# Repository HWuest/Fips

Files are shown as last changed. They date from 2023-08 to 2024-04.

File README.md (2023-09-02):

# Fips
Fips, mobile communication device for deafblind people

Offen

## Motivation
The biggest problem for deafblind people is social isolation.
Ofcourse they can read books printed in Braille or write a letter using a Braille keyboard, but this is not the same as talking with somebody.
## The aim of the project
is to provide a technical solution which allows deafblind people to talk with somebody as similar to a normal talk as possible. 
## System architecture - Top Level
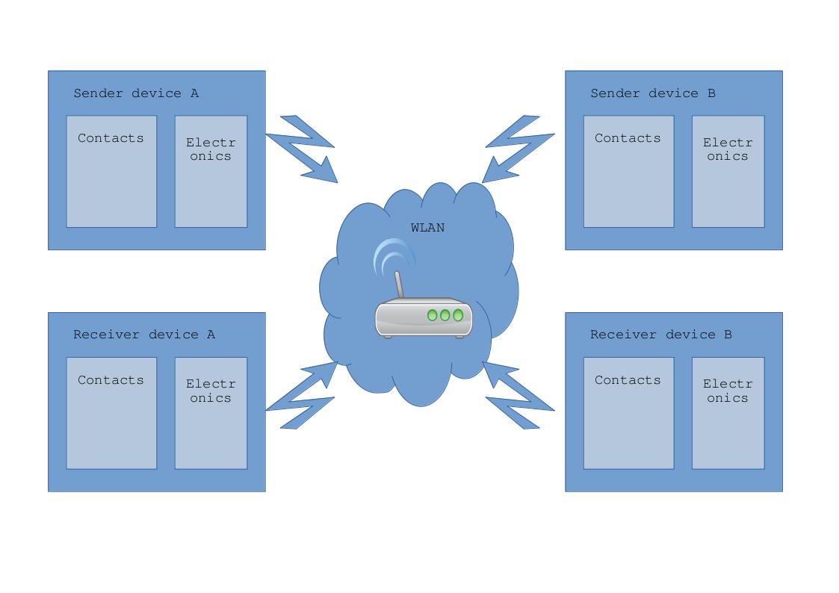
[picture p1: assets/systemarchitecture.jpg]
JPG image


## How to build

1. Get all hardware components from the partlist (see hardware folder)
2. Generate the 3D printing files for an available 3D printer from the .stl files in the 3D folder
3. Print the components (3 parts of the aktuators are needed 5 times)
4. Clue the magnets on the magnet holder and place them in the coil holder so that the magnet holder can move freely up and down in the coil holder
5. Clip the bootom of the coil holder on to the coil holder
6. Wind 500 windings of the cooper wire on each coil holder leaving two 5cm long wires outside for electrically connection
7. Remove the isolation half a centimeter from the ends of the wires (with sandpaper)
8. Test the functionality of the actuator with the battery and mark the polarity where the magnet moves upwards
9. Mount the charging electronics, the battery, the actuators, the switches and the microcontroller in the housing
10. Connect the electronic components and the driver IC acording to the schematic (see hardware folder)
11. Download the SW on the microcontroller -> [Link to description](bin/Readme.md)
12. Test the functionality: inputs done with the switches on the input side should imediatly be mirrored on the actuators on the output side
13. Fix all parts with screws and put the housing together, finaly fix it with screws

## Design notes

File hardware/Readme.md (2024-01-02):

## Hardware
We have a sender and a receiver device.

The schematics are fips-sender.pdf and fips-receiver.pdf.

The sender device has a printed circuit board for easier connection of parts.

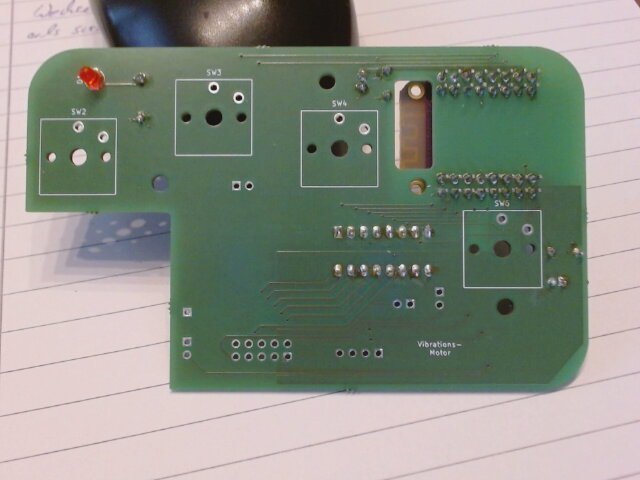
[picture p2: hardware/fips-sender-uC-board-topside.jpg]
top side
The top side of the board holds the keys and a LED (keys not shown in the picture 

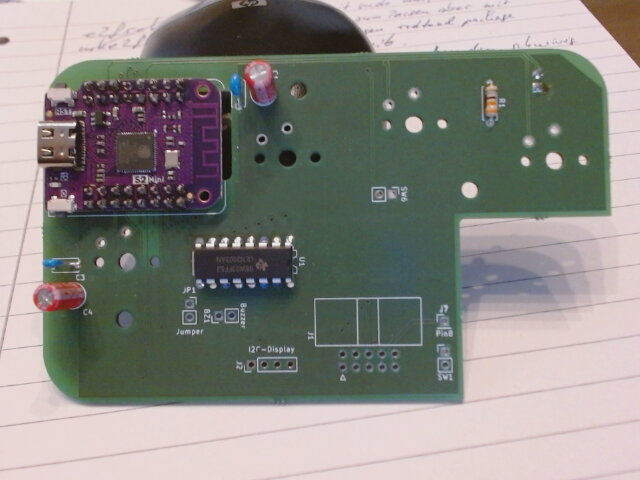
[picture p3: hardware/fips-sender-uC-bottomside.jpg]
top side
The bottom side holds the ESP32 microcontroller board and some other components.

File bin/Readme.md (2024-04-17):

## Latest ready to use binaries to flash on a ESP32S2 mini microcontroller board
- DeafBlind.bin
- bootloader.bin
- partition-table.bin
- (optional) ota_data_initial.bin 

## Beschreibung für das Flashen der Software (Programmierung des Mikrocontrollers)
Das Flashen der Software besteht aus mehreren Schritten.
- Das Flashen des Fips Programms für den ESP32, DeafBlind.bin
- Das Flashen des bootloaders, bootloader.bin
- Das Flashen der partition table, partition-table.bin
- (optional) Das Flashen von ota_data_inbitial.bin 
- Das Flashen der Dateien für die Webseiten auf dem ESP32
 
Zuerst müssen aber die Dateien vom github Server auf den lokalen Computer kopiert werden.
Dazu erst einen Ordner auf dem lokalen Computer anlegen, in dem alle notwendigen Dateien abgelegt werden sollen. 
Dann auf dieser Seite die Datei DeafBlind.bin anklicken. Dann oben rechts auf Download klicken und den Ordner auf dem lokalen Computer auswählen.
Wenn die Datei in den Download Ordner gespeichert wurde, die Datei von hier in den gewünschten Ordner ziehen.
Als zweites und drittes mit den Dateien bootloader.bin und partition-table.bin genauso verfahren. 

Zum Flashen des Fips Programms braucht man ein spezielles Flash Tool der Fa. Espressif. Es ist ein Python Programm und heisst esptool.py.
Die Installationsanweisung ist unter folgendem Link zu finden
`https://docs.espressif.com/projects/esptool/en/latest/esp32/installation.html#installation`

Bei Windows braucht man noch den Python Interpreter, damit sehen die Installationsschritte wie folgt aus.

1. Python installieren. Den Installer findet man unter `https://www.python.org/downloads/windows/`. Bei der Installation das Häkchen für die Anpassung der `PATH` Variablen setzen.
2. Das "esptool" installieren. Dazu mit `CMD` ein Terminal Fenster unter Windows aufmachen und folgenden Befehl eingeben: ```pip install esptool```.   

(Wir empfehlen, unser Script `fips-esptool` zu verwenden oder anzupassen, wenn die Dateien in anderen Ordnern liegen.)
```
python3 -m esptool --chip esp32s2 -b 460800 --before=default_reset --after=hard_reset write_flash --flash_mode dio --flash_freq 80m --flash_size 4MB 0x1000 bootloader.bin 0x10000 DeafBlind.bin 0x8000 partition-table.bin
```
oder optional mit ota - over the air - Programmierung: 

```
python3 -m esptool --chip esp32s2 -b 460800 --before=default_reset --after=hard_reset write_flash --flash_mode dio --flash_freq 80m --flash_size 4MB 0x1000 bootloader.bin 0x10000 DeafBlind.bin 0x8000 partition-table.bin 0xe000 ota_data_initial.bin
```

> Unter Linux ist Python standardmässig bereits installiert. Hier muss nur noch das esptool mit dem gleichen Kommando wie oben installiert werden. Eine > mögliche Fehlerquelle ist noch die installierte Python version, sie sollte grösser V3.7 sein. Die installierte Version erhält man mit dem Aufruf von `python --version` in der Kommandozeile. Wenn eine ältere Python Version installiert ist, kann man auf eine aktuelle Version upgraden, es sein denn.man braucht die ältere Version aus anderen Gründen. Ist das der Fall, gibt es kein Standard Vorgehen.  

Das Programm sucht automatisch nach dem richtigen USB Port. Wenn es den nicht findet und eine entsprechende Fehlermeldung ausgibt, kann man den Port explizit als zusätzliche Option `--port xyz` angeben. Unter Windows heisst der port COMx, wobei x eine Zahl ist. Unter Linux heisst der port /dev/ttyACMx, wobei x wieder eine Zahl ist. 

**Linux**
```
--port /dev/ttyACM0
```

**Windows** 
```
--port com4
```
#### Flashen der Dateien für die Webseiten
Nach dem Flashen des Programms "DeafBlind.bin" kann das Programm mit einem Reset des ESP32 gestartet werden. Dabei erstellt das Programm einen WLAN Access Point mit der IP Adresse 192.168.4.1 und der WLAN ssid DB.

Zuerst muss man das WLAN wechseln, aus dem eigenen WLAN in das WLAN, das der ESP32 aufgespannt hat. Der eigene Computer zeigt unter WLAN Einstellungen die sichtbaren WLAN Netze an. Man deaktiviert das bisherige WLAN und meldet sich bei dem WLAN mit dem Namen DB neu an.

Die Zugangsdaten sind:
- ssid: DB
- Password: 123456789  

Der Aufruf der initialen Webseite erfolgt in einem beliebigen Webbrowser mit der Adresszeile ```https://192.168.4.1/index.html```.

> Der Webbrowser meldet eine unsichere Seite. Bestätigen, dass man trotzdem mit der Seite verbunden werden möchte.
> ( Es ist unser eigener Server, also alles in Ordnung ) 
Man sieht dann folgende Seite: 

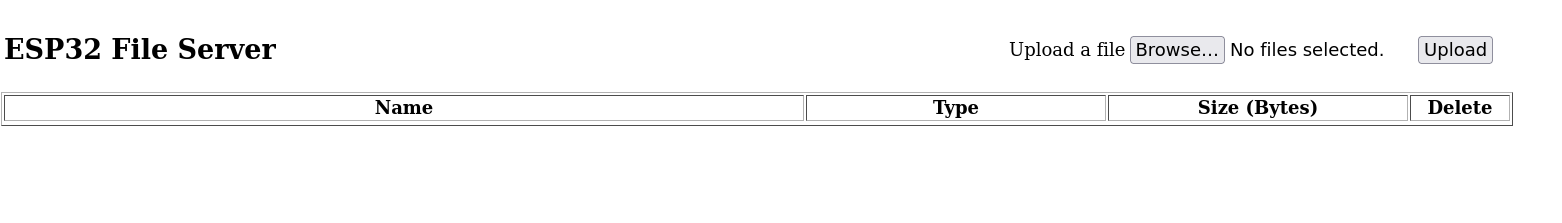
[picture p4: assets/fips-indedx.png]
image index


Hier kann man man über den `BROWSE` Tab die u.g. Dateien auswählen und durch Anklicken des `UPLOAD` Felds laden. 

Vorher noch die Dateien für die Webseiten in einen Ordner auf dem eigenen Rechner laden. Die Dateien finden sich auf der Github Seite in folgendem Ordner:
```
software/DeafBlind/webpages
```

**Liste der Dateien**
- Home.html
- Home.js
- Setup.html
- Setup.js
- Config.js
- DHSHMenu.css
- DHSHMenu.js
- DHSsocket.js
- ILGH16XB.FNT
- ILGH24XB.FNT
- ILGH32XB.FNT
- LATIN32B.FNT
- index.html

Die Datei index.html als letztes laden, danach ändert sich die Webseite.

#### Konfiguration für das eigene lokale WLAN
Nach dem man alle o.g. Dateien hochgeladen hat, sollte man den ESP32 erneut resettten, um alle Änderungen wirksam zu machen.

Erneuter Aufruf mit der Adresszeile ```http://192.168.4.1``` zeigt jetzt eine neue Seite:

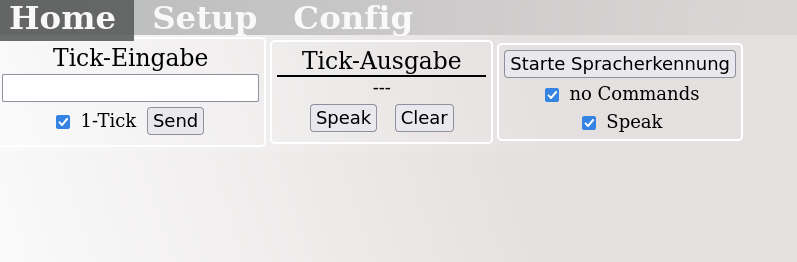
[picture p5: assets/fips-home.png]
image home


Mit dem Tab `SETUP` wechseln wir zur Setup Seite. In dem Feld `WLAN Credentials` setzen wir unsere eigenen lokalen WLAN Einstellungen oder das WLAN, in dem wir uns gerade befinden und das Gerät nutzen wollen mit `IP-Adresse-des-Routers,WLAN-Passwort` also z.B. `192.168.1.0,a6bH!vK#`.

Die Schaltflächen `Senden` und `Speichern` nacheinander anklicken, um die Änderungen zu übernehmen und abzuspeichern. Danach ist das Gerät betriebsbereit und meldet sich selbständig im lokalen Netzwerk an.

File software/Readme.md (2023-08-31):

# Software for ESP32S2 microcontroller

The SW can be build with the Espressif IDF 5.0.1.
It uses several Espressif SW components, manely the Espressif mesh-lite mesh network component which is used for the intercommunication of the devices.

(REQUIRES driver fatfs vfs nvs_flash esp_wifi lwip esp_timer esp_https_server mdns esp_lcd_touch_xpt2046 esp_websocket_client app_update ssd1306 iot_bridge mesh_lite)

The SW is written in C++ using the following architecture:
[SW_Architektur.pdf](https://github.com/HWuest/Fips/files/12486967/SW_Architektur.pdf)

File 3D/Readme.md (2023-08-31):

# 3D Data for printing the Fips-Device housing with a 3D-printer

The housing consist of the output part on the left side including the five output actuators, the battery, some electronics and the on/off switch connected to the input part on the right side which includes the five input switches and the microcontroller and the input switches.
Housing open


The five actuators are constructed with a small magnet clued on a magnet holder placed in a coil holder with 500 windings of a 0,125mm cooper wire.



Housing closed

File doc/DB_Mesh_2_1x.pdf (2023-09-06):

# DeafBlind Mesh Benutzerhandbuch

## Software Version V2.1x ESP32 S2 Mini

### - DHS Desert Hard- & Software Dr. Harald Wüst 06.09.2023

- Seite 2

# DeafBlind Mesh

### Software Version V2.1x ESP32 S2 Mini

2. AUFBAU EINES GERÄTE-NETZWERKS...3
3.1. ZEICHENSATZWECHSEL ( SCH SCH ).....4

- Seite 3
1. Einleitung
2. Aufbau eines Geräte-Netzwerks

Für ein Geräte-Netzwerk ist ein DeafBlind-Gerät als Server erforderlich. Weitere
DeafBlind-Geräte | können | sich | damit
Verbinden und so ein Kommunikations-Netwerk aufbauen.

Nach dem einschalten des ersten Gerätes (keine Verbindung zu einem bestehenden Netzwerk möglich) wir dieses automatisch zum DeafBlind-Server für andere Geräte.

Der | DeafBlind | Server | versucht | dann
maximal | 1 | Minute | lang | eine | WLan-
Verbindung zu einem bekannten WLan-Netz herzustellen. Während dieser Zeit blinkt die Geräte-LED.

Der Verbindungsstatus (1. Gerät im Netz D-Tick, 2. Gerät Z-Tick, …) durch eine kurze Tick-Ausgabe angezeigt (1. Gerät im
Netz | D-Tick, | Verbindung | zu | einem
bestehenden Netzwerk Z-Tick).

War der Verbindungsaufbau zum WLAN-Rooter erfolgreich kann Die Web-Seite des DeafBlind-Netzwerks über Eingabe von „deafblind.local“ als URL (nicht auf Apple-Geräten) bzw. über die Geräte IP-Adresse als URL mit jedem Web-Browser erreicht werden.

Das Gerät öffnet auch einen WiFi Acces-Point. Dieser hat den Namen „DB“ mit dem Passwort 123456789.

Nach | Verbindung | eines | Gerätes | (z.B.
Smart-Phone) mit dem Access-Point kann mit einem Web-Browser eine beliebige Web-Adresse (z.B. xyz.com) aufgerufen
werden. Es | erfolgt | eine automatische
Weiterleitung auf die DefaBlind Server WebSeite.

Wird danach ein Gerät in Reichweite des DeafBlind Netzwerkes eingeschaltet baut
dieses | direkt | eine | Verbindung | zum
Netzwerk auf. Alle Eingabe werden dann auf alle verbundenen Geräte im Netzwerk in Echtzeit übertragen.
3. Tick Eingabe

Das Tick-Gerät dient der Eingabe einzelner Zeichen aus dem DeafBlind Zeichensatz
sowie | der | Eingabe | spezieller | weiterer
Komandos. Dazu müssen die Finger einer Hand die fünf Tasten des Gerätes im
richtigen | Muster | möglichst | gleichzeitig
drücken. Den Buchstaben ‚a‘ erhält man
z.B. | durch | Drücken | der | ganz | links
liegenden Taste (bei der rechten Hand unter dem Daumen). Für ein ‚h‘ muss man die vier rechten Tasten drücken (und die linke Taste unter dem Daumen loslassen).
Dabei | sollten | die | Finger | möglichst
gleichzeitig die Tasten drücken (die Zeit bis zu der alle Taste gedrückt sein müssen kann eingestellt werden, siehe Tick s-Komando).

Eine solche Eingabe eines Zeichens wird im Folgenden als ‚Tick‘ bezeichnet.

Für die Eingabe weiterer Zeichen können
die | Tasten | entweder | kurz | vollständig
freigegben oder (bei gleichen Teilen des Musters) nur die zu ändernden Tasten gedrückt werden.

Die eingegebenen Zeichen werden dann sofort an alle Teilnehmer des Netzwerkes gesendet und an der Tick-Ausgabe bzw. im Web-Browser und dem seriellen Interface ausgegeben. Das Zeichen wird auch auf
der | eigenen | Tick-Ausgabe | als
Rückmeldung ausgegeben.

Die Tasten werden von links nach rechts im Weiteren so benannt:

D (aumen),
Z (eigefinger),
M (ittelfinger),
R (ingfinger),
K (leiner Finger)

- Seite 4

Nicht gedrückte Tasten werden durch Striche ‚--‚ gekennzeichnet.

Das Zeichen ‚h‘ vom obigen Beispiel entspricht damit dem Tick

-- Z M R K | -> | h

Hinweis: Da alle Eingaben direkt an alle Teilnehmer weiter gegeben werden kann es bei einer größeren Anzahl Teilnehmer schnell zu durcheinander kommen. Dies ist identisch mit dem durcheinander reden bei einer sprachlichen Unterhaltung und kann durch Disziplin der Teilnehmer reduziert werden.

3.1. Zeichensatzwechsel ( sch sch )

Der Standard-Zeichensatz ist folgender:

a | D -- -- -- -- | | b | -- Z -- -- K
c | D – M R K | | d | D – M -- --
e | -- Z -- -- -- | | f | D Z -- R --
g | D – M R -- | | h | -- Z M R K
i | -- -- M -- -- | | j | D Z M – K
k | D -- -- R -- | | l | -- -- M R --
m | -- Z – R -- | | n | D Z -- -- --
o | -- -- -- R -- | | p | D Z -- -- K
q | -- Z M -- R | | r | D Z M R --
s | -- -- -- R K | | t | -- Z M -- --
u | -- -- -- -- K | | v | D Z -- R K
w | D -- M -- K | | x | -- Z -- R K
y | D -- -- -- K | | z | -- -- M – K
ä | D Z M -- -- | | ö | -- Z M R –
ü | -- -- M R K | ch D -- -- R K
sch | D Z M R K
Über | einen | ‚sch | sch‘ | Doppel-Tick
(Zeichensatzwechsel sch: D M Z R K) kann
auf weitere | Zeichensätze | umgeschaltet
werden:

1 2 3 4 5 6 7 8 …

A B C D E F G …

Mit jedem Zeichensatzwechsel Doppel-Tick wird zwischen den Zeichensätzen im Kreis gewechselt. Da die Zeichenwechsel-Ticks
ebenfalls | an | die | anderen | Teilnehmer
übermittelt werden sind diese über den
aktuell | aktiven | Zeichensatz | informiert
(abhängig vom Ausgabe-Modus, siehe m-Kommando).

Der neue Zeichensatz bleibt jeweils nur für das nächste Zeichen aktiv und wird dann wieder automatisch auf Normal zurück gesetzt.

Mit der Tick-Eingabe

sch sch sch sch h a l l o

ergibt sich daher die Ausgabe

H a l l o

da | durch | zwei | Mal | ‚sch‘ | auf | die
Großbuchstaben umgeschaltet wurde.
Um | die | Umschaltung | dauerhaft | zu
aktivieren | (um | z.B. | eine | längere
Zahlenfolge einzugeben) muss nach der Wahl des Zeichensatzes ein einzelner Kommando- Tick ‚ch‘ gegeben werden (siehe Kap. 4):

sch sch ch a e n i

gibt die Ausgabe

1 2 3 4

Mit dem nächsten Zeichensatz-Tick sch
sch | wird | wieder | auf | den | Standard
Zeichensatz zurück geschaltet.

Hinweis: Im Normal-Modus (siehe m-Kommand) kann eine zwischenzeitliche Tick-Eingabe eines anderen Teilnehmers die Umschaltung auf den dritten Zeichensatz und/oder die dauerhafte Aktivierung des Zeichensatzes stören (da dazu 2 direkt aufeinander folgende Ticks erforderlich sind).

- Seite 5
4. Tick Kommando ( ö ö )

Mit dem ‚ö ö‘ Doppel-Tick (Kommando-Tick ö: -- Z M R --) können Kommandos ausgeführt werden. Damit lassen sich diverse Funktionen des Gerätes steuern wobei die anderen Teilnehmer über alle Steuer-Kommandos durch die Kommando-Zeichen Sequenz informiert sind (abhängig vom Ausgabe-Modus, siehe m-Kommando).

Hinweis: Im Normal-Modus (siehe m-Kommando) kann eine zwischenzeitliche Tick-Eingabe eines anderen Teilnehmers die Kommando-Ausführung
stören | oder zur Aktivierung | eines falschen
Kommandos führen (da dazu 3 direkt aufeinander folgende Ticks erforderlich sind).

Es gibt folgende Tick Kommandos:

4.1. m Ausgabe-Modus

Ändern des Ausgabe-Modus.
Im Standard Ausgabe-Modus (0) werden
alle | Zeichen | incl. | Kommandozeichen
ausgegeben. Im Reduzierten Modus (1) werden die Kommandozeichen unterdrückt damit die Text-Ausgabe nicht gestört wird. Dieser Modus kann zum Schreiben von Texten benutzt werden.

Hinweis: Im reduzierten Modus sehen andere Teilnehmer die Kommando-Eingaben nicht und
kennen | daher | Änderungen | an | der
Systemkonfiguration | nicht | mehr.

Sende „Return“ (Zeilenrücklauf / neue Zeile) an die verbundenen Geräte.

Alle | seit | dem | letzten | Zeilenwechsel
gesendeten | Zeichen | werden | in | einem
Zeilen-Speicher | für | die | weitere
Verwendung zwischengespeichert (siehe e-Kommando).
Es wird kein Zeichen an die Tick-Geräte gesendet. Im Browser sowie auf der Seriellen Schnittstelle wird eine neue Zeile begonnen.
4.2. n | Neue Zeile
Sendet | einen | Zeilenumbruch | an | die
verbundenen Geräte. Der Zeilenumbruch
wird | nicht | als | Tick | ausgegeben. | Im
Browser und der seriellen Schnittstelle wird eine neue Zeile begonnen um die
Lesbarkeit | für | nicht | Taubblinde | zu
verbessern.
Zusätzlich werden alle Zeichen die seit dem letzten Zeilenumbruch eingegeben wurden in einem Zeilen-Speicher für die
Verwendung | mit | dem | e-Kommando
gespeichert. | Auf diese | Weise | können
Taubblinde über das Tick-Eingabegerät
Zeilen-Kommandos | erstellen | und
ausführen (siehe e-Kommando Kap. 4.5).
4.3. z Leerzeichen

Sendet ein „ “ (Leerzeichen) an die
verbundenen | Geräte.
Das Leerzeichen wird nicht als Tick ausgegeben. Im Browser und der seriellen Schnittstelle erscheint ein Leerzeichen zur besseren Lesbarkeit für nicht Taubblinde.
4.4. l letztes Zeichen löschen

Löscht das letzte Zeichen. Im Browser und
der | seriellen | Schnittstelle | wird | zur
besseren Lesbarkeit für nicht Taubblinde das letzte Zeichen gelöscht.
4.5. e Zeile ausführen

Ausführen einer gespeicherten Zeile (siehe n- Kommando Kap.4.2).
Über | diese | Funktion | können | Zeilen-
Kommandos (siehe Kap. 4) über ein Tick-Gerät ausgeführt werden indem zuerst eine neue Zeile über das n-Kommando gestartet
wird, | dann | das | gewünschte | Zeilen-
Kommando | mit | dem | Tick-Gerät | in
Einzelbuchstaben geschrieben und die Zeile mit einem weiteren n-Kommando abgeschlossen wird.
Das Zeilen-Kommando wird damit in den Zeilen-Speicher übertragen und kann als Ganzes über das e- Kommando ausgeführt werden.

- Seite 6
4.6. t Trainings-Modus

Startet den Trainings-Modus.
Beginnend mit dem Buchstaben ‚a‘ werden
nacheinander | alle | Zeichen | des | Fips-
Alphabets ausgegeben und auf Eingabe des erkannten Zeichens gewartet.
Ist | das | eingegebene | Zeichen | falsch
(Ausgabe | wurde | falsch | erkannt | oder
Eingabe war nicht korrekt) wird das Zeichen 2 mal kurz hintereinander erneut ausgegeben um den Fehler anzuzeigen und
dann | das | gleiche | Zeichen | für | einen
weiteren Versuch neu präsentiert.
Ist das eingegebene Zeichen richtig werden in schneller Folge nacheinander alle 5 Aktuatoren angesteuert um den Erfolg anzuzeigen. Danach wird das nächste Zeichen ausgegeben bis alle Zeichen richtig erkannt wurden.
Beim initialen Start des Trainings-Modus wird dies durch 3 malige schnelle Ausgabe des Buchstabens ‚a‘ angezeigt.
Durch Eingabe des Kommandozeichens ‚ö‘
kann | der | Trainings-Modus jeder | Zeit
unterbrochen werden.
Die | Schwierigkeit | kann | über | die
Ausgabegeschwindigkeit | variiert | werden
(siehe Zeilenkommando x, Kap. 5.3).
5. Zeilen Kommandos

Kommando-Eingaben mit mehr als einem Zeichen (diese können über das Serielle
Interface | oder | die | Web-Seite | direkt
eingegeben werden) werden als Zeilen-Kommandos interpretiert.

Folgende Funktionen stehen dabei zur Verfügung:

5.1. s: s 100

Ändern der Tick Stabilisierungszeit in Millisekunden.
Die angegebene Zeit bestimmt wie schnell einzelne Zeichen über das Tick-Gerät eingegeben werden können (maximale Zeit vom Drücken der ersten Taste bis zum Drücken aller benötigten Tasten). Hohe
Werte | ermöglichen | eine | sicherere
Bedienung, niedrige Werte ein schnelleres Schreiben. Die Werte sollten zwischen 50 (max. 10 Zeichen/s) und 250ms (max. 2 Zeichen/s) liegen.

Hinweis: Die Zeit wird in der Konfiguration gespeichert (siehe p-Kommando).

5.2. d: | d 5
Ändern | der | Tick | Pulse-Dauer | (in
Millisekunden).
Die angegebene Zeit bestimmt wie lange
ein | Zeichen | über | das | Tick-Gerät
ausgegeben wird (Dauer der Aktivierung). Hohe Werte ermöglichen eine sichere Erkennung, niedrige Werte ein schnelleres Lesen bei erschwerter Erkennung. Die Werte sollten zwischen 10 und 250ms liegen.
Hinweis: Die Zeit wird in der Konfiguration gespeichert (siehe p-Kommando).
5.3. x: x 500

Ändern der Ausgabegeschwindigkeit der Zeichen einer Textzeile (in Millisekunden). Die angegebene Zeit bestimmt wie schnell hintereinander die einzelnen Zeichen bei der automatischen Ausgabe einer längeren Textzeile aufeinander folgen. Hohe Werte
ermöglichen | eine | sichere | Erkennung,
niedrige Werte ein schnelleres Lesen. Die Werte sollten zwischen 10 (100 Zeichen/s)
und | 1000ms | (1 | Zeichen/s) | liegen.
Hinweis: Die Zeit wird in der Konfiguration gespeichert (siehe p-Kommando).
5.4. o: o text

Automatische Ausgabe des angegebenen Textes an alle verbundenen Geräte.

- Seite 7

Die Ausgabe erfolgt mit der eingestellten Geschwindigkeit (siehe x-Kommando) als käme sie von einem Tick-Gerät (alle
enthaltenen | Kommando-Zeichen | (siehe
Tick Kommando) werden ausgeführt).
5.5. r: r r

Neustart (Reboot) des Gerätes.
Alle Einstellungen werden auf die in ap.cfg gespeicherte Konfiguration zurückgesetzt
(siehe | p-Kommando) | und | die
Netzwerkverbindung neu aufgebaut.
5.6. g: g g

Die letzte gespeicherte Konfiguration wird geladen.

5.7. p: | p p
Die | aktuelle | Konfiguration | wird
gespeichert.
Die Konfiguration wird bei jedem Start des
Gerätes | als | Standard-Konfiguration
geladen die daher hiermit geändert werden kann.
5.8. t: t 5

Tick-Modus einstellen.
Das | erste | Bit | im | angegebenen | Wert
bestimmt, ob ein Tick erkannt und die Stabilisierungszeit (siehe s-Kommando) bei jeder Änderung abgewartet wird (0) oder nur wenn Tasten zusätzlich gedrückt werden (1). Damit kann nach einem kurzen Abheben einzelner Finger schneller ein neues Zeichen eingegeben werden, es können aber keine neuen Zeichen nur durch abheben von Fingern generiert werden.
Das | zweite | Bit | gibt | an, | ob | die
Stabilisierungszeit ab der ersten Tick-
Änderung | unabhängig | von | weiteren
Änderungen abläuft (schnelle Eingabe, nicht so robust bei nacheinander Setzen mehrere Finger) oder ob diese bei jeder Änderung innerhalb der Stabilisierungszeit neu beginnt (langsamer, robuster).
5.9. m: m 77

Mesh-ID einstellen.
Geräte mit der gleichen Mesh-ID bilden
zusammen | ein | Mesh-Netzwerk. | Durch
Wahl einer | anderen | Mesh-ID können
mehrere | Mesh-Netzwerke | unabhängig
voneinander im gleichen Raum arbeiten so dass getrennte Gespräche geführt werden können.

- Seite 8
6. Kommando Kurz-Übersicht

sch 2 x D M Z R K nächster Zeichensatz (gefolgt von ö: dauerhafte Umschaltung)

ö 2 x -- M Z R -- leitet Tick Kommando ein:

6.1. Tick
m: | Ausgabe Modus wechseln
l: | letztes Zeichen löschen
z: | Leerzeichen schreiben
n: | Neue Zeile (letzte Zeile speichern)
e: | Gespeicherte Zeile ausführen
t: | Trainings-Modus starten
r: | Routerless Modus aktivieren
6.2. Zeilen
s: | Stabilisierungszeit
d: | Pulsdauer
x: | Ausgabegeschwindigkeit
o: | Textausgabe
r: | Neustart
g: | Konfiguration laden
p: | Konfiguration speichern
t: | Tick-Modus einstellen
m: | Mesh-ID einstellen
7. 1. / Standard Zeichensatz
a | D -- -- -- -- | b | -- Z -- -- K
c | D -- M R K | d | D -- M -- --
e | -- Z -- -- -- | f | D Z -- R --
g | D -- M R -- | h | -- Z M R K
i | -- -- M -- -- | j | D Z M -- K
k | D -- -- R -- | l | -- -- M R --
m | -- Z -- R -- | n | D Z -- -- --
o | -- -- -- R -- | p | D Z -- -- K
q | -- Z M -- -- | r | D Z M R --
s | -- -- -- R K | t | -- Z M -- --
u | -- -- -- -- K | v | D Z -- R K
w | D -- M -- K | x | -- Z -- R K
y | D -- -- -- K | z | -- --M -- K
ä | D Z M -- -- | ö | -- Z M R --
ü | -- -- M R K | ch | D -- -- R K
sch | D Z M R K
7.1. 2. Zeichensatz
1 | a | D -- -- -- -- | ) | b | -- Z -- -- K
@ | c | D – M R K | 5 | d | D – M -- --
2 | e | -- Z -- -- -- | + | f | D Z -- -- --
: | g | D – M R -- | % | h | -- Z M R K
4 | i | -- -- M -- -- | ? | j | D Z M – K
9 | k | D -- -- R -- | - | l | -- -- M R --
0 | m | -- Z – R -- | 3 | n | D Z -- -- --
8 | o | -- -- -- R -- | < | p | D Z -- -- --
. | q | -- Z M -- -- | & | r | D Z M R --
{ | s | -- -- -- R K | 6 | t | -- Z M -- --
/ | u | -- -- -- -- K | $ | v | D Z – R K
, | w | D -- M -- K | } | x | -- Z – R K
( | y | D -- -- -- K | > | z | -- -- M -- K
7 | ä | D Z M -- -- | = | ö | -- Z M R –
ü | ü | -- -- M R K | ch | | D -- -- R K
sch | | D Z M R K
7.2. 3. Zeichensatz
A | D -- -- -- -- | B | -- Z -- -- K
C | D – M R K | D | D – M -- --
E | -- Z -- -- -- | F | D Z -- R --
G | D – M R -- | H | -- Z M R K
I | -- -- M -- -- | J | D Z M – K
K | D -- -- R -- | L | -- -- M R --
M | -- Z – R -- | N | D Z -- -- --
O | -- -- -- R -- | P | D Z -- -- K-
Q | -- Z M -- -- | R | D Z M R --
S | -- -- -- R K | T | -- Z M -- --
U | -- -- -- -- K | V | D Z -- R K
W | D -- M -- K | X | -- Z -- R K
Y | D -- -- -- K | Z | -- -- M – K
Ä | D Z M -- -- | Ö | -- Z M R –
Ü | -- -- M R K | ch | D -- -- R K
sch | D Z M R K

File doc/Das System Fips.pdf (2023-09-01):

## Ein neues taktiles Kommunikationssystem für taubblinde, bzw. hörsehbehinderte Personen

Taubblindheit ist eine der folgenschwersten Behinderungen überhaupt. In Deutschland leben ca. 6.000 bis 10.000 taubblinde Personen. Etwa 60 % davon sind über 60 Jahre alt.
Mit nur drei Sinnen müssen sie ihr Leben meistern. Eine einflussreiche Lobby haben sie nicht.
Die taubblinden Personen signalisieren immer wieder, dass sie am allermeisten am Mangel an unabhängiger Information und Kommunikation leiden.

Mithilfe von taktilen Kommunikationsformen wie taktiles Gebärden oder der Fingersprache Lormen können Taubblinde zwar in Echtzeit und synchron Informationen austauschen, sind aber an räumliche Nähe gebunden.
Technische Hilfsmittel wie die Braillezeile helfen hingegen schon distanzunabhängig zu arbeiten und asynchron mit anderen Menschen zu kommunizieren, so z.B. mit der Gerätekombination Tabli, ein Produkt der Firma Helptech.

Eine Möglichkeit hingegen in Echtzeit und synchron, aber distanzunabhängig Informationen auszutauschen und somit auch über große Entfernungen hinweg ein möglichst realitätsnahes Gespräch zu führen, gestaltet sich mit dem aktuellen Stand der Technik schwierig.
Mit dem System FiPS wird ein neuer Weg beschritten, taubblinde Menschen zu vernetzen, in die Gesellschaft zu integrieren und ihnen mehr Selbstbestimmtheit zu ermöglichen.

Kurzbeschreibung des System FiPS (Five PointS)

Das System FiPS ist eine andere Art des Lormens, wobei die Schwierigkeiten einer digitalen Übertragung überbrückt werden. FiPS besteht aus zwei Geräteteilen, einem Ein- und einem Ausgabeteil.
Mit den fünf Fingern der rechten Hand werden in eine Tastatur mit fünf Tasten (wie in eine Hand) die Buchstabenkombinationen eingegeben, sozusagen gelormt (gefipst).
Fünf Aktoren (kleine Stifte) lormen (fipsen) die Buchstaben in einem zweiten Gerät auf die Fingerkuppen der anderen Hand. Schreiben und Lesen (Sprechen und Hören) geschieht mit beiden Händen.
Bei der Kommunikation ist kein Wechsel der Hände zwischen Sprechen und Hören nötig. Ermüdungserscheinungen können dadurch wesentlich verringert werden.
Die digitale Technik hilft diese Gespräche in Echtzeit auch über beliebige Entfernungen zu übertragen.

Beim Fips-Alphabet werden die fünf Tasteneingaben kombiniert und können so 31 verschiedene Zeichen darstellen. Darin sind die 26 Buchstaben des deutschen Alphabetes, die Umlaute und ch und sch enthalten. Sonderzeichen und Programmierbefehle können durch mehrmaliges Drücken einer Taste erzeugt werden.

Das neue System ermöglicht es, dass mehrere Nutzer gemeinsam einer Unterhaltung, bzw. einem Vortrag folgen (Spracheingabe), in Echtzeit Rückfragen stellen und geordnet antworten können. Sogar die Übermittlung von Stimmungen und Gefühlen durch kleine Unterschiede bei der taktilen Eingabe, ist bei geübten Personen zu erwarten. Das könnte z.B. durch Variation der Eingabegeschwindigkeit entstehen.
Außerdem besteht durch FiPS die Möglichkeit, auf einfache Art und Weise durch Texte zu kommunizieren. Der Text kann über FiPS, über eine zusätzliche optische Anzeige oder über Sprachausgabe einer App ausgegeben werden. Das ist zugleich für mehrere Personen mit unterschiedlichen Sinneswahrnehmungen möglich. Spracheingabe ist ebenfalls über die App möglich. FiPS ist auf taktile Sprache ausgelegt, die Bedienung eines PC ist damit nicht vorgesehen.

FiPS dürfte das Potential haben, zu einem universellen Kommunikationsgerät im Alltag von taubblinden, bzw. hörsehbehinderten Personen zu werden.

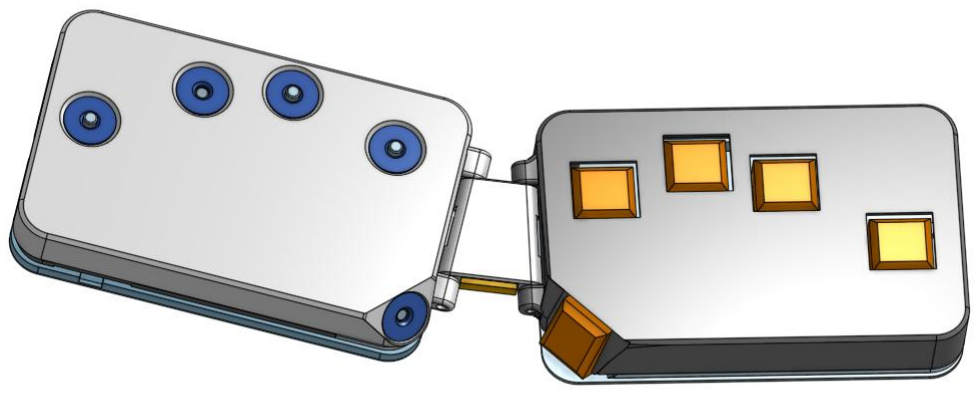
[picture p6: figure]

Erstinformationen zum System FiPS:

Bernd Hönicke, Bornweg 9, 35080 Bad Endbach
Tel.: 02776-9227372, Mobil: 0151-17500621, Mail: gb.hoenicke@web.de

Weiterführende Informationen:

Die Verbreitung als open-source mit der Gerätehardware aus dem 3D-Drucker über die Maker-Comunity/Makerspaces und damit die kostengünstige Verfügbarkeit weltweit ohne Notwendigkeit einer kommerziellen Gewinnerwirtschaftung erfolgt über den Link: https://github.com/HWuest/Fips. Damit kann ein Selbstbau oder ein Bau mit Unterstützung von Makerspaces erfolgen. Adressen von Makerspaces, Unterstützung beim Aufbau sowie der Bezug von Bausätzen oder Prototypen-Fertiggeräten ist auf Anfrage möglich.

Ansprechpartner: | Dr. Harald Wüst, | Mail: harald.wuest@gmx.net.
| Thomas Kranz, | Mail: thomas-kranz@gmx.de

Stand: 31.08.2023

# FiPS-Alphabet

Darstellung der Eingabeseite (Schreiben), rechte Hand
1 = Daumen, 2 = Zeigefinger, 3 = Mittelfinger, 4 = Ringfinger, 5 = kleiner Finger Das Alphabet zur Ausgabeseite (Hören), linke Hand, ist dazu spiegelbildlich.
27 | ä | l | l | l | | | c | l | | l | l | l
28 | ö | | l | l | l | | v | l | l | | l | l
29 | ü | | | l | l | l | j | l | l | l | | l
30 | ch | l | | | l | l | h | | l | l | l | l
31 | sch | l | l | l | l | l | sch | l | l | l | l | l
| FiPS | | FiPS
| alphabetisch | | systematisch
| | 1 | 2 | 3 | 4 | 5 | | 1 | 2 | 3 | 4 | 5
1 | a | l | | | | | a | l
2 | b | | l | | | l | e | | l
3 | c | l | | l | l | l | i | | | l
4 | d | l | | l | | | o | | | | l
5 | e | | l | | | | u | | | | | l
6 | f | l | l | | l | | n | l | l
7 | g | l | | l | l | | t | | l | l
8 | h | | l | l | l | l | l | | | l | l
9 | i | | | l | | | s | | | | l | l
10 | j | l | l | l | | l | d | l | | l
11 | k | l | | | l | | k | l | | | l
12 | l | | | l | l | | y | l | | | | l
13 | m | | l | | l | | m | | l | | l
14 | n | l | l | | | | b | | l | | | l
15 | o | | | | l | | z | | | l | | l
16 | p | l | l | | | l | ä | l | l | l
17 | q | | l | l | | l | f | l | l | | l
18 | r | l | l | l | l | | p | l | l | | | l
19 | s | | | | l | l | g | l | | l | l
20 | t | | l | l | | | w | l | | l | | l
21 | u | | | | | l | ch | l | | | l | l
22 | v | l | l | | l | l | q | | l | l | | l
23 | w | l | | l | | l | ö | | l | l | l
24 | x | | l | | l | l | x | | l | | l | l
25 | y | l | | | | l | ü | | | l | l | l
26 | z | | | l | | l | r | l | l | l | l

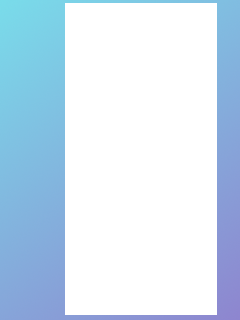
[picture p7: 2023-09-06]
software/DeafBlind/webpages/Background.png

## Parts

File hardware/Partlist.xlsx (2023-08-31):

Number | Part | Description | Price | Data | Source
1 | Esp32 s2 mini | Microcontroller | 3.00 € |  | de.aliexpress.com
2 | M1,7 Schraube | Schraube | 0.05 € | Kunstoffschraube für ESP32
5 | Kailh low profile ultradünn RGB Swithes | Taster | 4.00 € |  | https://de.aliexpress.com/item/32838369089.html
5 | Kailh choc niedrigen profil 1u blank keycap | Kappen | 1.50 € |  | https://de.aliexpress.com/item/32949747794.html
1 | Kabel | Kabel | 0.10 €
5 | Scheibenmagnet Ø 6,0 x 3,0 mm | Magnet | 2.00 € |  | https://www.magnet-shop.net/neodym-magnete/scheibenmagnete/scheibenmagnet-6.0-x-3.0-mm-n45-nickel-haelt-900-g
1 | ULN2003A | Treiber-IC | 0.10 € |  | https://de.aliexpress.com/item/1005003758885390.html
1 | 3D-Druckfilament ca. 150g | 3D-Teile | 4.00 €
1 | Kupferlackdraht 0,125mm ca. 100m / 12g | Spulendraht | 4.00 € |  | https://www.schneitec-shop.com/kupferlackdraht-o-0-125mm-w210-grad-2.html
4 | M3 X 15mm Schraube | Schraube | 0.20 € | Gewindeschraube für Halter
1 | USB-C Kabel | Stromkabel | 1.00 €
1 | LED transparent, 5mm | Lichtleiter | 0.05 € | Nur obere Hälfte als Lichtleiter | https://de.aliexpress.com/item/33015212696.html?spm
 | Material |  | 20.00 €
 | Optional Akku, Vibration
1 | Micro/Typ-C USB 5V 2,4 EIN Dual USB 18650 | Ladeschaltung | 1.00 € | 5V DC/DC, >1A | https://de.aliexpress.com/item/1005001692510053.html
1 | Lithium-Batterie 3,7 V 705075 3200mah | Battery | 7.00 € | 3.7V LiPo, <1.5mm | https://de.aliexpress.com/item/4000064953093.html
1 | 4mm Mini 3Pin Löcher Kippschalter | Schalter | 0.95 € |  | https://de.aliexpress.com/item/1005002282341641.html
2 | M1,7 Schraube | Shraube | 0.05 € | Kunstoffschraube für Ladesch.
1 | Vibrationsmotor 1234 12mm Durchmesser | Vibrationsmotor | 1.00 € |  | https://de.aliexpress.com/item/1005003252937718.html
 | Material Optional |  | 10.00 €
 | Gesamt |  | 30.00 €

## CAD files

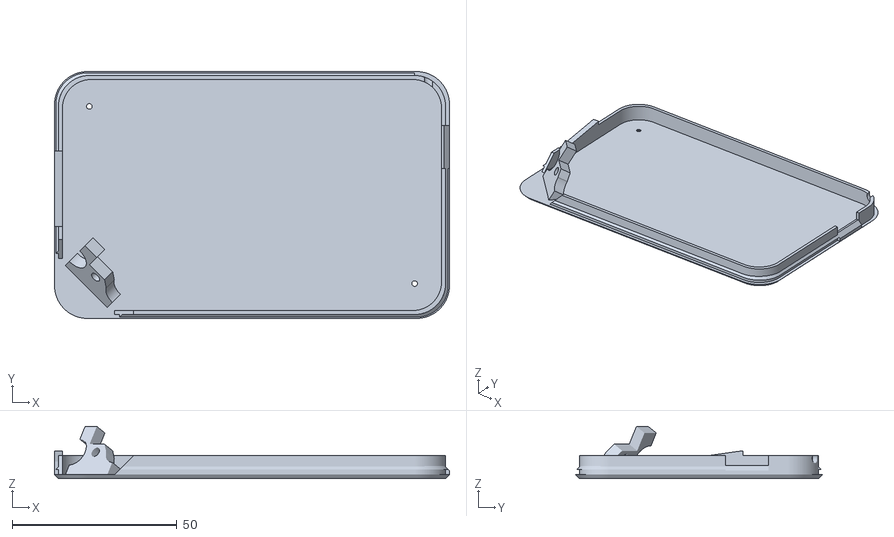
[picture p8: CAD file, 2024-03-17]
3D/Input_Bottom.stl
120.0 x 75.0 x 15.9

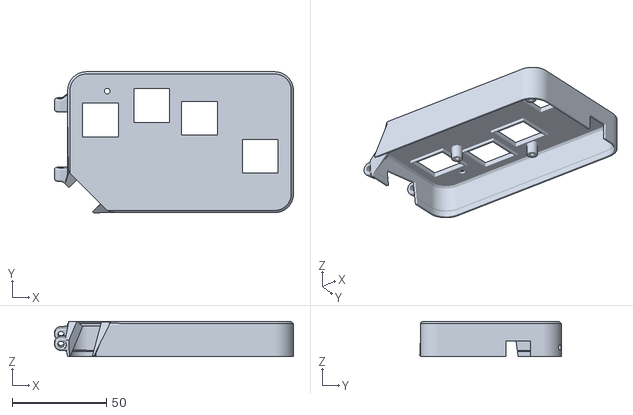
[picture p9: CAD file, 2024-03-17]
3D/Input_Top.stl
127.0 x 75.2 x 18.8

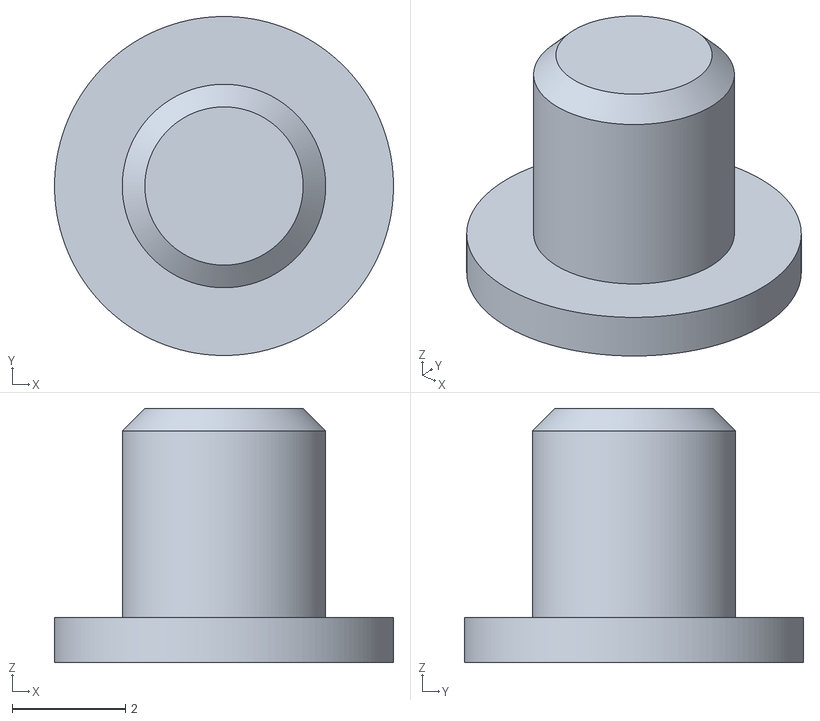
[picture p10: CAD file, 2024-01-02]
3D/Mag_Holder.stl
6.00 x 6.00 x 4.50

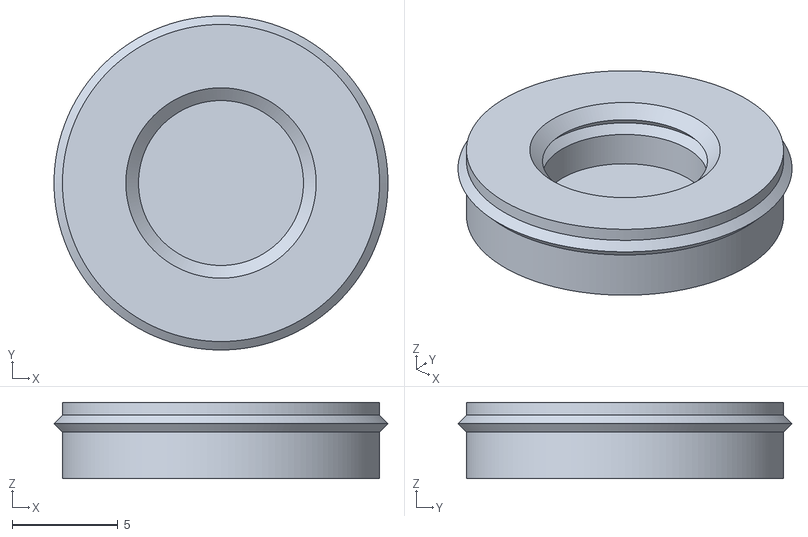
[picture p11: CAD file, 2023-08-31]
3D/Coil_Bottom.stl
15.8 x 15.8 x 3.60

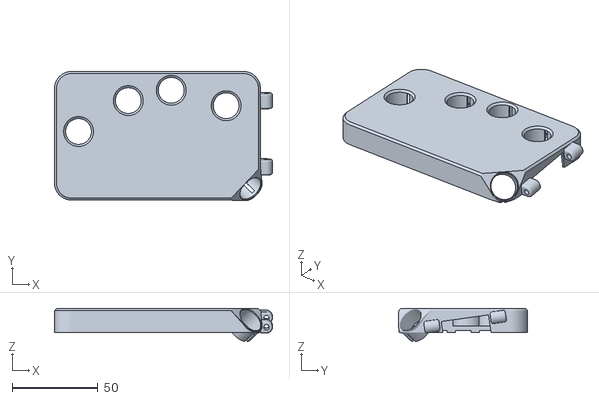
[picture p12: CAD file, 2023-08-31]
3D/Output_top.stl
127.0 x 75.3 x 19.2

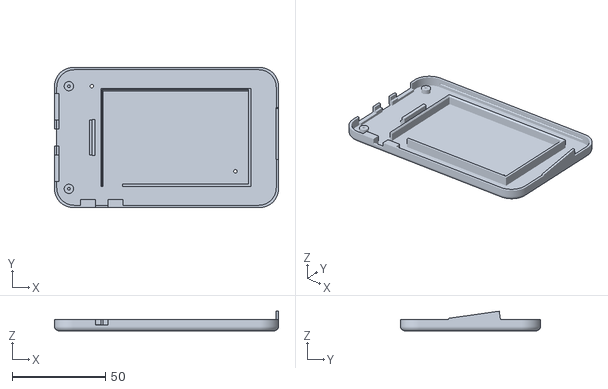
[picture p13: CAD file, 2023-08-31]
3D/Accu_Housing_Bottom.stl
120.0 x 75.0 x 10.5

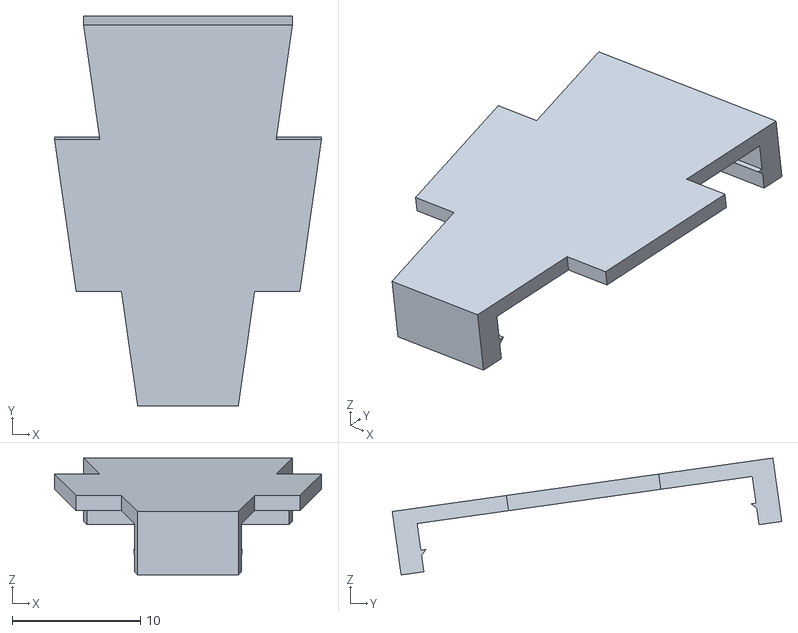
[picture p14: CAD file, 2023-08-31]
3D/Verbinder_Deckel_Clipin.stl
20.8 x 30.4 x 9.13

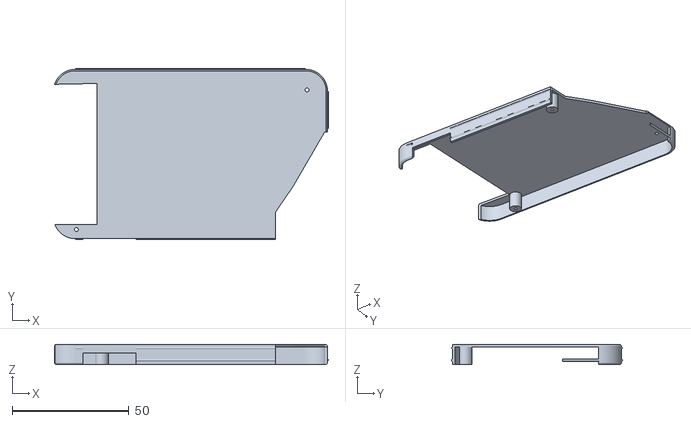
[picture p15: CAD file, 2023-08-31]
3D/Accu_Top_Clipin.stl
117.5 x 73.4 x 8.70

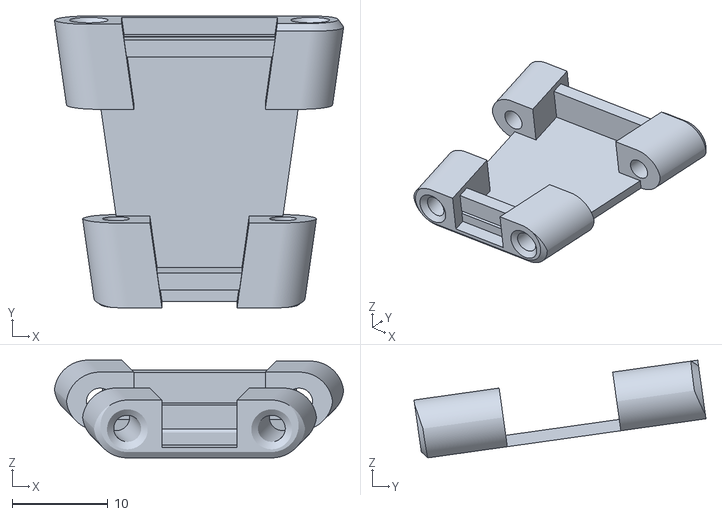
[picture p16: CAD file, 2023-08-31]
3D/Verbinder.stl
30.3 x 30.6 x 10.2

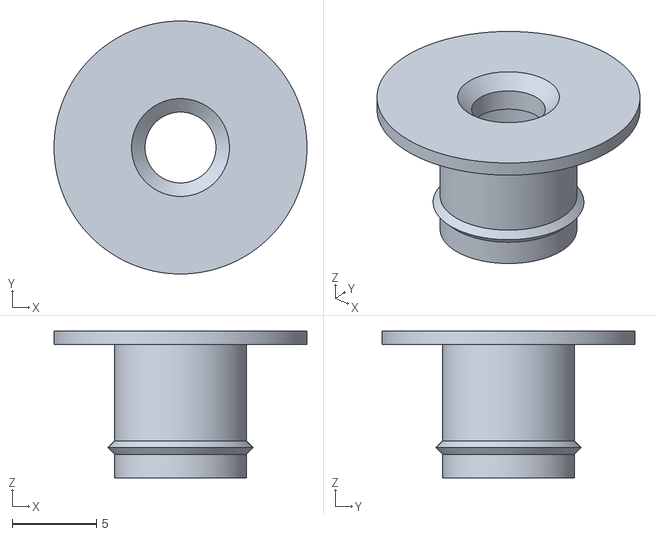
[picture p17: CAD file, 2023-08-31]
3D/Coil_Holder.stl
15.0 x 15.0 x 8.70

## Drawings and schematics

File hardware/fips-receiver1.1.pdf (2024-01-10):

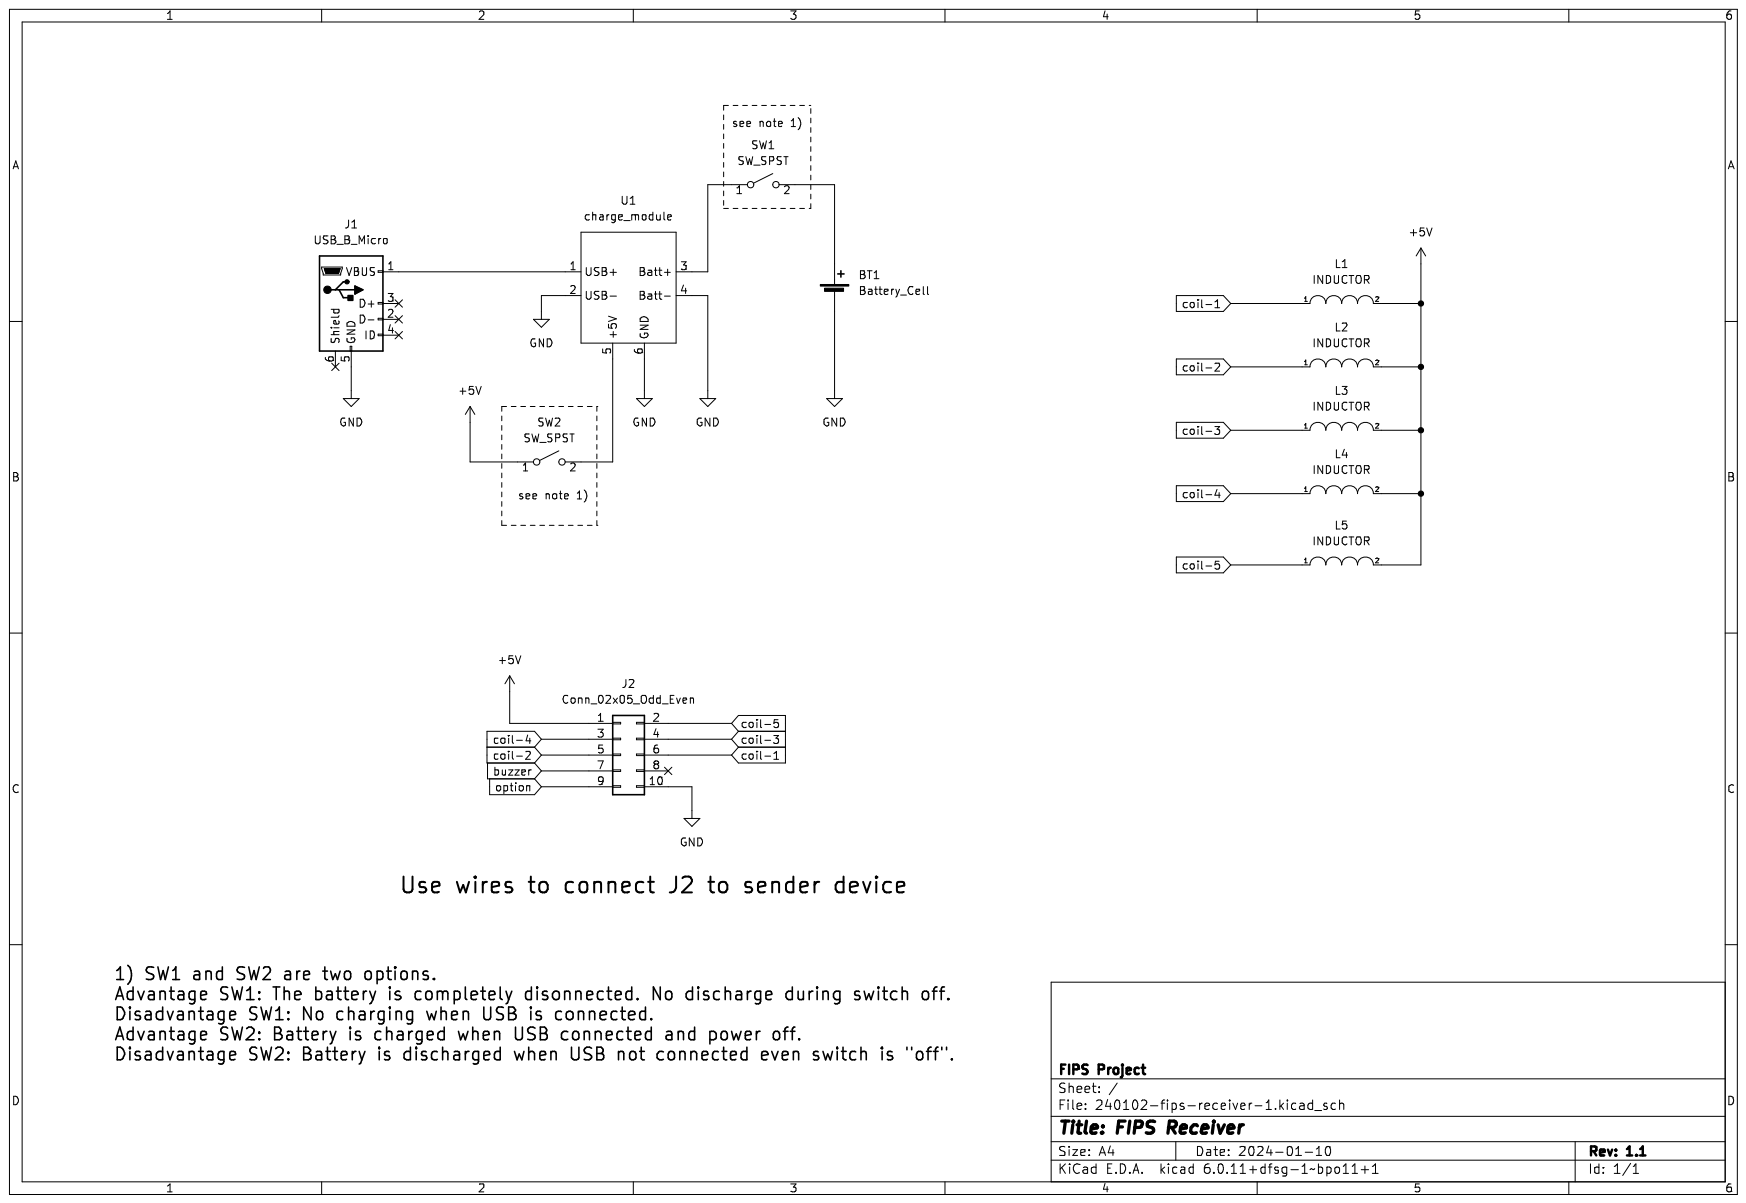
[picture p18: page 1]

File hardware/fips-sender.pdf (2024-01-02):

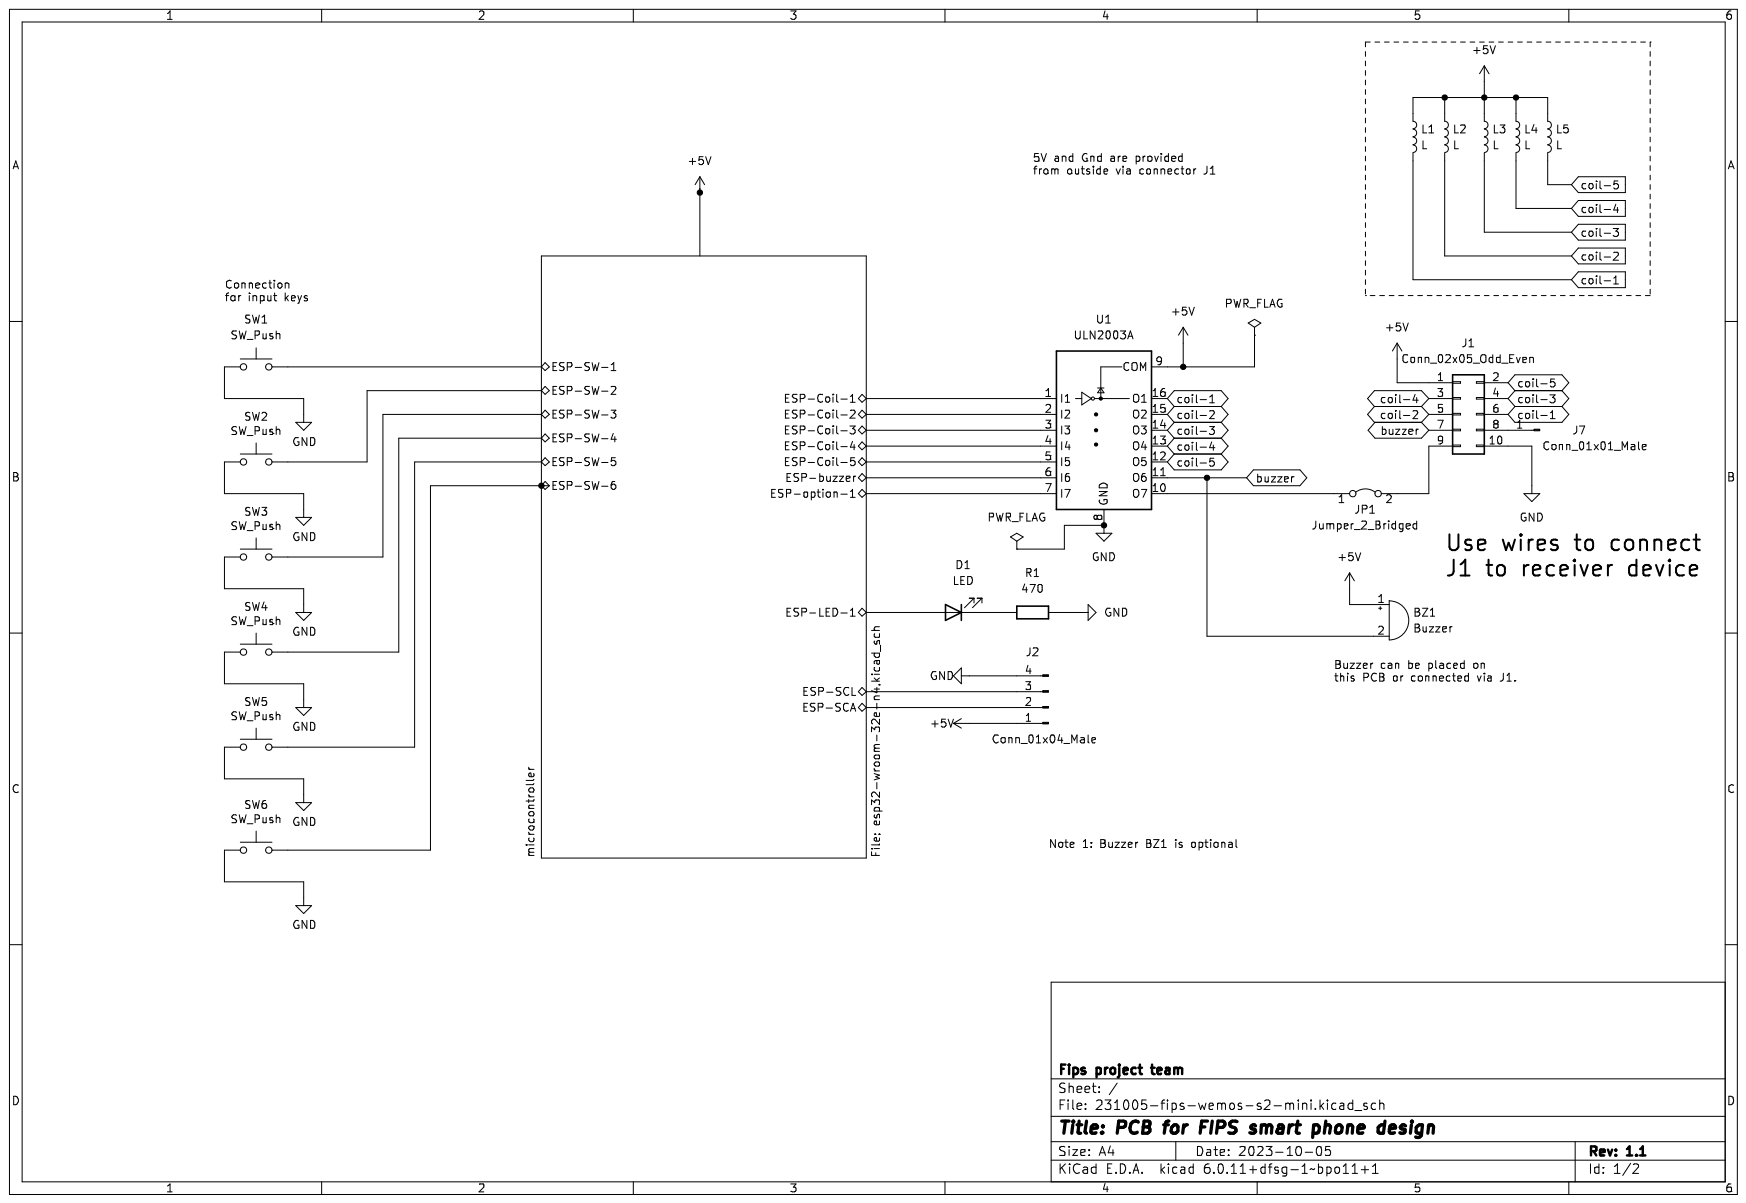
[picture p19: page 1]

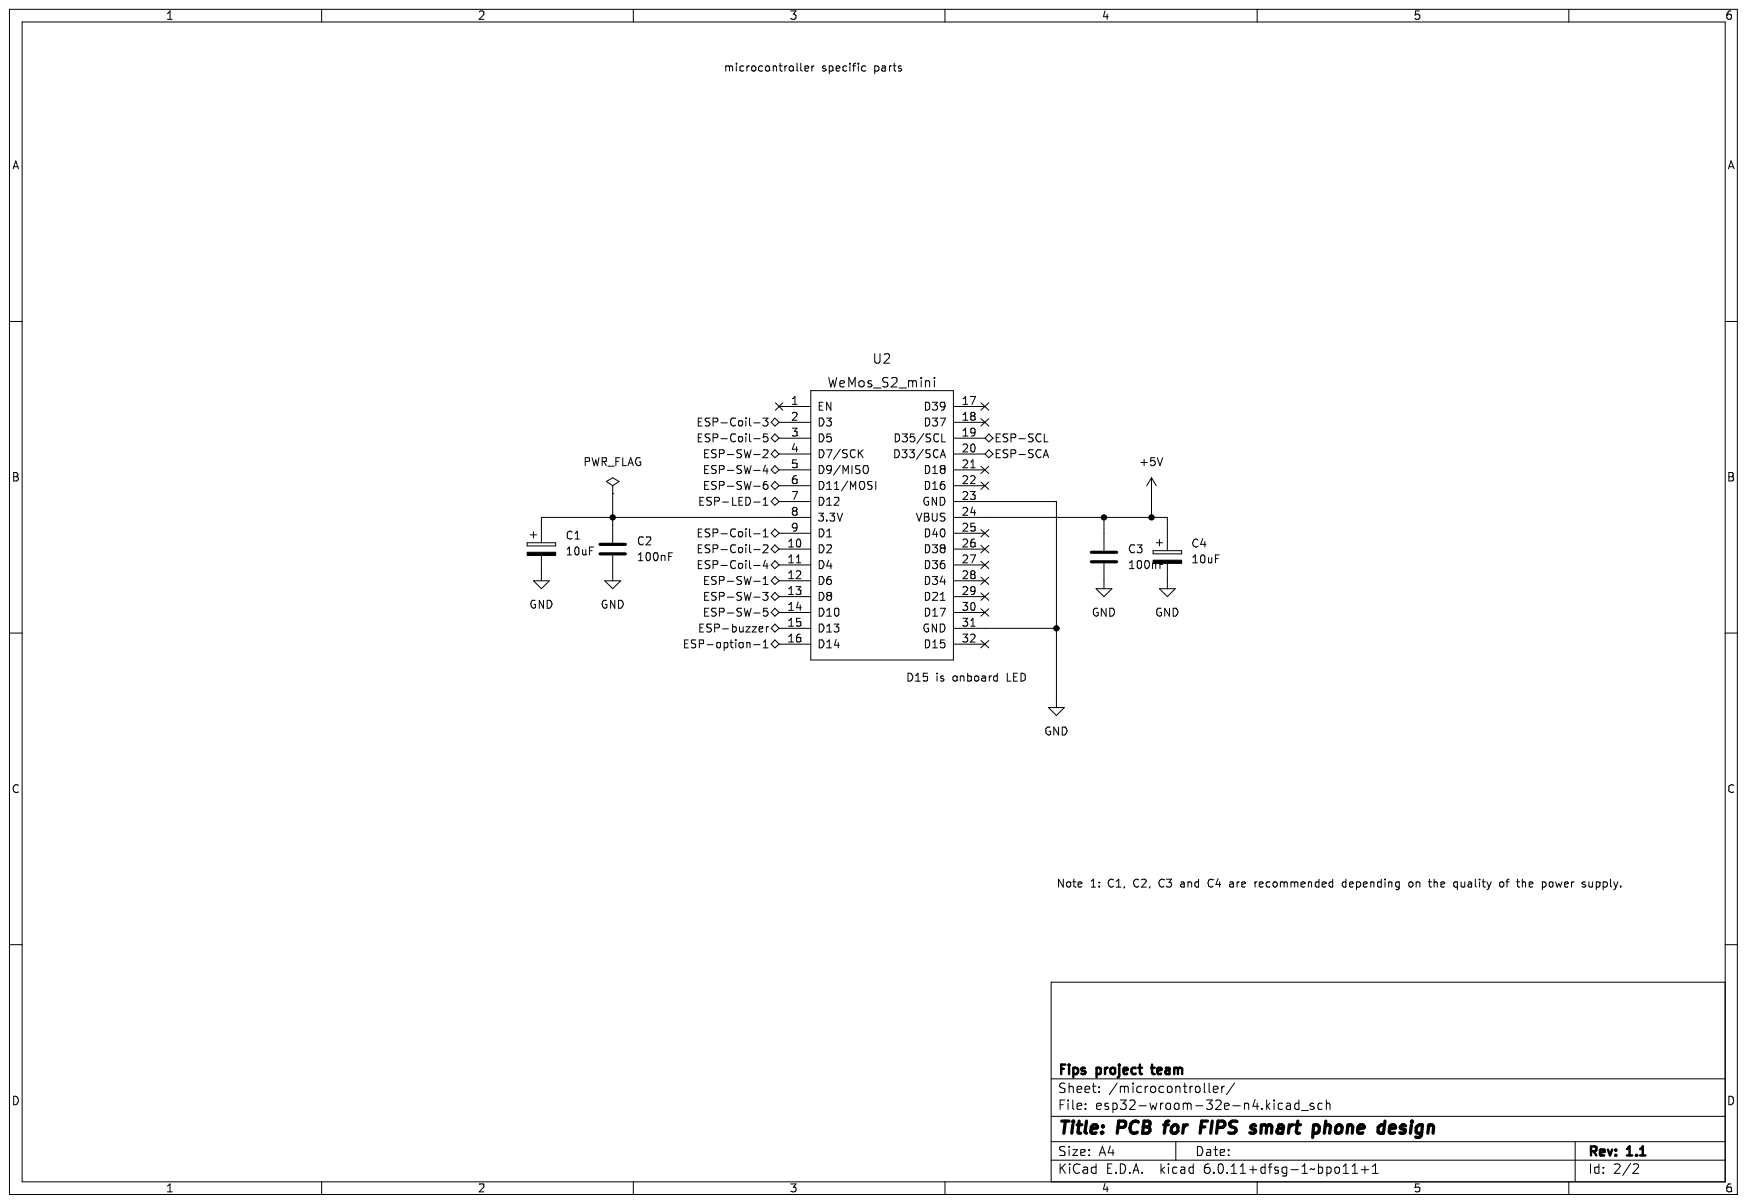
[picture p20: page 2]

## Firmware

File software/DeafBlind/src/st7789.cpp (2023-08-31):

#include <string.h>
#include <inttypes.h>
#include <math.h>

#include "freertos/FreeRTOS.h"
#include "freertos/task.h"

#include <driver/spi_master.h>
#include <driver/gpio.h>
#include "esp_log.h"

#include "st7789.h"

#define TAG "ST7789"
#define	_DEBUG_ 0

#if 0
#ifdef CONFIG_IDF_TARGET_ESP32
#define LCD_HOST HSPI_HOST
#elif defined CONFIG_IDF_TARGET_ESP32S2
#define LCD_HOST SPI2_HOST
#elif defined CONFIG_IDF_TARGET_ESP32S3
#define LCD_HOST SPI2_HOST
#elif defined CONFIG_IDF_TARGET_ESP32C3
#define LCD_HOST SPI2_HOST
#endif
#endif

#if CONFIG_SPI2_HOST
#define HOST_ID SPI2_HOST
#elif CONFIG_SPI3_HOST
#define HOST_ID SPI3_HOST
#endif

static const int SPI_Command_Mode = 0;
static const int SPI_Data_Mode = 1;
//static const int SPI_Frequency = SPI_MASTER_FREQ_20M;
//static const int SPI_Frequency = SPI_MASTER_FREQ_26M;
static const int SPI_Frequency = SPI_MASTER_FREQ_40M;
//static const int SPI_Frequency = SPI_MASTER_FREQ_80M;

void spi_master_init(TFT_t * dev, int16_t GPIO_MOSI, int16_t GPIO_SCLK, int16_t GPIO_CS, int16_t GPIO_DC, int16_t GPIO_RESET, int16_t GPIO_BL)
{
	esp_err_t ret;

	ESP_LOGI(TAG, "GPIO_CS=%d",GPIO_CS);
	if ( GPIO_CS >= 0 ) {
		//gpio_pad_select_gpio( GPIO_CS );
		gpio_reset_pin( (gpio_num_t) GPIO_CS );
		gpio_set_direction( (gpio_num_t) GPIO_CS, GPIO_MODE_OUTPUT );
		gpio_set_level( (gpio_num_t) GPIO_CS, 0 );
	}

	ESP_LOGI(TAG, "GPIO_DC=%d",GPIO_DC);
	//gpio_pad_select_gpio( GPIO_DC );
	gpio_reset_pin( (gpio_num_t) GPIO_DC );
	gpio_set_direction( (gpio_num_t) GPIO_DC, GPIO_MODE_OUTPUT );
	gpio_set_level( (gpio_num_t) GPIO_DC, 0 );

	ESP_LOGI(TAG, "GPIO_RESET=%d",GPIO_RESET);
	if ( GPIO_RESET >= 0 ) {
		//gpio_pad_select_gpio( GPIO_RESET );
		gpio_reset_pin( (gpio_num_t) GPIO_RESET );
		gpio_set_direction( (gpio_num_t) GPIO_RESET, GPIO_MODE_OUTPUT );
		gpio_set_level( (gpio_num_t) GPIO_RESET, 1 );
		vTaskDelay(10);
		gpio_set_level( (gpio_num_t) GPIO_RESET, 0 );
		vTaskDelay(10);
		gpio_set_level( (gpio_num_t) GPIO_RESET, 1 );
		vTaskDelay(10);
	}

	ESP_LOGI(TAG, "GPIO_BL=%d",GPIO_BL);
	if ( GPIO_BL >= 0 ) {
		//gpio_pad_select_gpio(GPIO_BL);
		gpio_reset_pin((gpio_num_t) GPIO_BL);
		gpio_set_direction( (gpio_num_t) GPIO_BL, GPIO_MODE_OUTPUT );
		gpio_set_level( (gpio_num_t) GPIO_BL, 0 );
	}

	ESP_LOGI(TAG, "GPIO_MOSI=%d",GPIO_MOSI);
	ESP_LOGI(TAG, "GPIO_SCLK=%d",GPIO_SCLK);
	spi_bus_config_t buscfg = {
		.mosi_io_num = GPIO_MOSI,
		.miso_io_num = 12,
		.sclk_io_num = GPIO_SCLK,
		.quadwp_io_num = -1,
		.quadhd_io_num = -1,
		.max_transfer_sz = 0,
		.flags = 0
	};

//	ret = spi_bus_initialize( HOST_ID, &buscfg, SPI_DMA_CH_AUTO );
//	ESP_LOGD(TAG, "spi_bus_initialize=%d",ret);
//	assert(ret==ESP_OK);

	spi_device_interface_config_t devcfg;
	memset(&devcfg, 0, sizeof(devcfg));
	devcfg.clock_speed_hz = SPI_Frequency;
	devcfg.queue_size = 7;
	devcfg.mode = 2;
	devcfg.flags = SPI_DEVICE_NO_DUMMY;

	if ( GPIO_CS >= 0 ) {
		devcfg.spics_io_num = GPIO_CS;
	} else {
		devcfg.spics_io_num = -1;
	}
	
	spi_device_handle_t handle;
	ret = spi_bus_add_device( HOST_ID, &devcfg, &handle);
	ESP_LOGD(TAG, "spi_bus_add_device=%d",ret);
	assert(ret==ESP_OK);
	dev->_dc = GPIO_DC;
	dev->_bl = GPIO_BL;
	dev->_SPIHandle = handle;
}


bool spi_master_write_byte(spi_device_handle_t SPIHandle, const uint8_t* Data, size_t DataLength)
{
	spi_transaction_t SPITransaction;
	esp_err_t ret;

	if ( DataLength > 0 ) {
		memset( &SPITransaction, 0, sizeof( spi_transaction_t ) );
		SPITransaction.length = DataLength * 8;
		SPITransaction.tx_buffer = Data;
#if 1
		ret = spi_device_transmit( SPIHandle, &SPITransaction );
#else
		ret = spi_device_polling_transmit( SPIHandle, &SPITransaction );
#endif
		assert(ret==ESP_OK); 
	}

	return true;
}

bool spi_master_write_command(TFT_t * dev, uint8_t cmd)
{
	static uint8_t Byte = 0;
	Byte = cmd;
	gpio_set_level( (gpio_num_t) dev->_dc, SPI_Command_Mode );
	return spi_master_write_byte( dev->_SPIHandle, &Byte, 1 );
}

bool spi_master_write_data_byte(TFT_t * dev, uint8_t data)
{
	static uint8_t Byte = 0;
	Byte = data;
	gpio_set_level( (gpio_num_t) dev->_dc, SPI_Data_Mode );
	return spi_master_write_byte( dev->_SPIHandle, &Byte, 1 );
}


bool spi_master_write_data_word(TFT_t * dev, uint16_t data)
{
	static uint8_t Byte[2];
	Byte[0] = (data >> 8) & 0xFF;
	Byte[1] = data & 0xFF;
	gpio_set_level( (gpio_num_t) dev->_dc, SPI_Data_Mode );
	return spi_master_write_byte( dev->_SPIHandle, Byte, 2);
}

bool spi_master_write_addr(TFT_t * dev, uint16_t addr1, uint16_t addr2)
{
	static uint8_t Byte[4];
	Byte[0] = (addr1 >> 8) & 0xFF;
	Byte[1] = addr1 & 0xFF;
	Byte[2] = (addr2 >> 8) & 0xFF;
	Byte[3] = addr2 & 0xFF;
	gpio_set_level( (gpio_num_t) dev->_dc, SPI_Data_Mode );
	return spi_master_write_byte( dev->_SPIHandle, Byte, 4);
}

bool spi_master_write_color(TFT_t * dev, uint16_t color, uint16_t size)
{
	//static
	uint8_t Byte[1024];
	int index = 0;
	for(int i=0;i<size;i++) {
		Byte[index++] = (color >> 8) & 0xFF;
		Byte[index++] = color & 0xFF;
	}
	gpio_set_level( (gpio_num_t) dev->_dc, SPI_Data_Mode );
	return spi_master_write_byte( dev->_SPIHandle, Byte, size*2);
}

// Add 202001
bool spi_master_write_colors(TFT_t * dev, uint16_t * colors, uint16_t size)
{
	//static
	uint8_t Byte[1024];
	int index = 0;
	for(int i=0;i<size;i++) {
		Byte[index++] = (colors[i] >> 8) & 0xFF;
		Byte[index++] = colors[i] & 0xFF;
	}
	gpio_set_level( (gpio_num_t) dev->_dc, SPI_Data_Mode );
	return spi_master_write_byte( dev->_SPIHandle, Byte, size*2);
}

void lcdInit(TFT_t * dev, int width, int height, int offsetx, int offsety)
{
	dev->_width = width;
	dev->_height = height;
	dev->_offsetx = offsetx;
	dev->_offsety = offsety;
	dev->_font_direction = DIRECTION90;
	dev->_font_fill = false;
	dev->_font_underline = false;

	spi_master_write_command(dev, 0x01);	//Software Reset
	vTaskDelay(5);

	spi_master_write_command(dev, 0x11);	//Sleep Out
	vTaskDelay(15);
	
	spi_master_write_command(dev, 0x3A);	//Interface Pixel Format
	spi_master_write_data_byte(dev, 0x55);
	//delayMS(10);
	
	spi_master_write_command(dev, 0x36);	//Memory Data Access Control
	spi_master_write_data_byte(dev, 0x00);

	spi_master_write_command(dev, 0x2A);	//Column Address Set
	spi_master_write_data_byte(dev, 0x00);
	spi_master_write_data_byte(dev, 0x00);
	spi_master_write_data_byte(dev, 0x00);
	spi_master_write_data_byte(dev, 0xF0);

	spi_master_write_command(dev, 0x2B);	//Row Address Set
	spi_master_write_data_byte(dev, 0x00);
	spi_master_write_data_byte(dev, 0x00);
	spi_master_write_data_byte(dev, 0x00);
	spi_master_write_data_byte(dev, 0xF0);

//	spi_master_write_command(dev, 0x21);	//Display Inversion On
//	delayMS(10);

	spi_master_write_command(dev, 0x13);	//Normal Display Mode On
	//delayMS(10);

	spi_master_write_command(dev, 0x29);	//Display ON
}

// Draw pixel
// x:X coordinate
// y:Y coordinate
// color:color
void lcdDrawPixel(TFT_t * dev, uint16_t x, uint16_t y, uint16_t color){
	if (x >= dev->_width) return;
	if (y >= dev->_height) return;

	uint16_t _x = x + dev->_offsetx;
	uint16_t _y = y + dev->_offsety;

	spi_master_write_command(dev, 0x2A);	// set column(x) address
	spi_master_write_addr(dev, _x, _x);
	spi_master_write_command(dev, 0x2B);	// set Page(y) address
	spi_master_write_addr(dev, _y, _y);
	spi_master_write_command(dev, 0x2C);	//	Memory Write
	spi_master_write_data_word(dev, color);
}

// Draw multi pixel
// x:X coordinate
// y:Y coordinate
// size:Number of colors
// colors:colors
void lcdDrawMultiPixels(TFT_t * dev, uint16_t x, uint16_t y, uint16_t size, uint16_t * colors) {
	if (x+size > dev->_width) return;
	if (y >= dev->_height) return;

	uint16_t _x1 = x + dev->_offsetx;
	uint16_t _x2 = _x1 + (size-1);
	uint16_t _y1 = y + dev->_offsety;
	uint16_t _y2 = _y1;

	spi_master_write_command(dev, 0x2A);	// set column(x) address
	spi_master_write_addr(dev, _x1, _x2);
	spi_master_write_command(dev, 0x2B);	// set Page(y) address
	spi_master_write_addr(dev, _y1, _y2);
	spi_master_write_command(dev, 0x2C);	//	Memory Write
	spi_master_write_colors(dev, colors, size);
}

// Draw rectangle of filling
// x1:Start X coordinate
// y1:Start Y coordinate
// x2:End X coordinate
// y2:End Y coordinate
// color:color
void lcdDrawFillRect(TFT_t * dev, uint16_t x1, uint16_t y1, uint16_t x2, uint16_t y2, uint16_t color) {
	if (x1 >= dev->_width) return;
	if (x2 >= dev->_width) x2=dev->_width-1;
	if (y1 >= dev->_height) return;
	if (y2 >= dev->_height) y2=dev->_height-1;

	ESP_LOGD(TAG,"offset(x)=%d offset(y)=%d",dev->_offsetx,dev->_offsety);
	uint16_t _x1 = x1 + dev->_offsetx;
	uint16_t _x2 = x2 + dev->_offsetx;
	uint16_t _y1 = y1 + dev->_offsety;
	uint16_t _y2 = y2 + dev->_offsety;

	spi_master_write_command(dev, 0x2A);	// set column(x) address
	spi_master_write_addr(dev, _x1, _x2);
	spi_master_write_command(dev, 0x2B);	// set Page(y) address
	spi_master_write_addr(dev, _y1, _y2);
	spi_master_write_command(dev, 0x2C);	//	Memory Write
	for(int i=_x1;i<=_x2;i++){
		uint16_t size = _y2-_y1+1;
		spi_master_write_color(dev, color, size);
#if 0
		for(j=y1;j<=y2;j++){
			//ESP_LOGD(TAG,"i=%d j=%d",i,j);
			spi_master_write_data_word(dev, color);
		}
#endif
	}
}

// Display OFF
void lcdDisplayOff(TFT_t * dev) {
	spi_master_write_command(dev, 0x28);	//Display off
}
 
// Display ON
void lcdDisplayOn(TFT_t * dev) {
	spi_master_write_command(dev, 0x29);	//Display on
}

// Fill screen
// color:color
void lcdFillScreen(TFT_t * dev, uint16_t color) {
	lcdDrawFillRect(dev, 0, 0, dev->_width-1, dev->_height-1, color);
}

// Draw line
// x1:Start X coordinate
// y1:Start Y coordinate
// x2:End   X coordinate
// y2:End   Y coordinate
// color:color 
void lcdDrawLine(TFT_t * dev, uint16_t x1, uint16_t y1, uint16_t x2, uint16_t y2, uint16_t color) {
	int i;
	int dx,dy;
	int sx,sy;
	int E;

	/* distance between two points */
	dx = ( x2 > x1 ) ? x2 - x1 : x1 - x2;
	dy = ( y2 > y1 ) ? y2 - y1 : y1 - y2;

	/* direction of two point */
	sx = ( x2 > x1 ) ? 1 : -1;
	sy = ( y2 > y1 ) ? 1 : -1;

	/* inclination < 1 */
	if ( dx > dy ) {
		E = -dx;
		for ( i = 0 ; i <= dx ; i++ ) {
			lcdDrawPixel(dev, x1, y1, color);
			x1 += sx;
			E += 2 * dy;
			if ( E >= 0 ) {
			y1 += sy;
			E -= 2 * dx;
		}
	}

	/* inclination >= 1 */
	} else {
		E = -dy;
		for ( i = 0 ; i <= dy ; i++ ) {
			lcdDrawPixel(dev, x1, y1, color);
			y1 += sy;
			E += 2 * dx;
			if ( E >= 0 ) {
				x1 += sx;
				E -= 2 * dy;
			}
		}
	}
}

// Draw rectangle
// x1:Start X coordinate
// y1:Start Y coordinate
// x2:End   X coordinate
// y2:End   Y coordinate
// color:color
void lcdDrawRect(TFT_t * dev, uint16_t x1, uint16_t y1, uint16_t x2, uint16_t y2, uint16_t color) {
	lcdDrawLine(dev, x1, y1, x2, y1, color);
	lcdDrawLine(dev, x2, y1, x2, y2, color);
	lcdDrawLine(dev, x2, y2, x1, y2, color);
	lcdDrawLine(dev, x1, y2, x1, y1, color);
}

// Draw rectangle with angle
// xc:Center X coordinate
// yc:Center Y coordinate
// w:Width of rectangle
// h:Height of rectangle
// angle:Angle of rectangle
// color:color

//When the origin is (0, 0), the point (x1, y1) after rotating the point (x, y) by the angle is obtained by the following calculation.
// x1 = x * cos(angle) - y * sin(angle)
// y1 = x * sin(angle) + y * cos(angle)
void lcdDrawRectAngle(TFT_t * dev, uint16_t xc, uint16_t yc, uint16_t w, uint16_t h, uint16_t angle, uint16_t color) {
	double xd,yd,rd;
	int x1,y1;
	int x2,y2;
	int x3,y3;
	int x4,y4;
	rd = -angle * M_PI / 180.0;
	xd = 0.0 - w/2;
	yd = h/2;
	x1 = (int)(xd * cos(rd) - yd * sin(rd) + xc);
	y1 = (int)(xd * sin(rd) + yd * cos(rd) + yc);

	yd = 0.0 - yd;
	x2 = (int)(xd * cos(rd) - yd * sin(rd) + xc);
	y2 = (int)(xd * sin(rd) + yd * cos(rd) + yc);

	xd = w/2;
	yd = h/2;
	x3 = (int)(xd * cos(rd) - yd * sin(rd) + xc);
	y3 = (int)(xd * sin(rd) + yd * cos(rd) + yc);

	yd = 0.0 - yd;
	x4 = (int)(xd * cos(rd) - yd * sin(rd) + xc);
	y4 = (int)(xd * sin(rd) + yd * cos(rd) + yc);

	lcdDrawLine(dev, x1, y1, x2, y2, color);
	lcdDrawLine(dev, x1, y1, x3, y3, color);
	lcdDrawLine(dev, x2, y2, x4, y4, color);
	lcdDrawLine(dev, x3, y3, x4, y4, color);
}
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

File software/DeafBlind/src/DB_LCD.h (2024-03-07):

/*
 * DB_LCD.h
 *
 *  Created on: 02.06.2023
 *      Author: HW
 *
 *  LCD Class for controlling small and large LCD in Deafblind application
 *  Depending on the Config settings lcd and lcdklein it is decided which LCD is present on HW side
 *
 *  Uses:
 *    DHS_Config, class to store information in Flash partition
 *    DHS_Mesh_lite, class to build mesh network
 *    DHS_1Tick_Control, class to control 1-tick Deafblind HW
 *    DHS_LCD, control large LCD display (class derived from)
 *    DHS_LCDklein, control samll LCD display (class derived from)
 *    DHS_FS, flash filesystem storage (has to be initialized before constructing DB_LCD)
 *
 *    esp_wifi, wifi functions
 *
 *  Defines:
 *    DHS_HEADLINE, Header-Text in display, should contain version information (less than 20 chars)
 */

#ifndef SRC_DB_LCD_H_
#define SRC_DB_LCD_H_

#define DHS_HEADLINE "DeafBlind FIPS 2.13" // Header-Text in display, should contain version information (less than 20 chars)

#include "DHS_1Tick_Control.h"
#include "DHS_Config.h"

#include "DHS_LCD.h"
#include "DHS_LCDklein.h"

#include "../src/DHS_Mesh_lite.h"
#include "esp_wifi.h"

class DB_LCD: public DHS_LCD, DHS_LCDklein {
  public:

   	DB_LCD(DHS_1Tick_Control *Cont, DHS_Config *Conf); // initialize LCD component

	void nodes(int n); 	// draw number of nodes on LCD
    void drawCharSet(); // draw current char set on LCD

  private:
	DHS_1Tick_Control *Controller; // command controller pointer
    DHS_Config 		  *Config;	   // config storage pointer

    int8_t numNodes = 0;    // number of connected nodes
    int layer 		= -1;   // layer of current node in mesh network
    int8_t iClients = 0;    // internet client connections
    int8_t touchActive = 0; // touch active counter
    int8_t outMode = 0;     // output mode on lcd
    uint8_t comMode = 0;    // command mode indicator

	int16_t xpos=0;	// current x char pos on display
	int16_t ypos=0; // current y char pos on display

    char charSetChars[3][31]={"abcdefghijklmnopqrstuvwxyz\x84\x94\x81*","1234567890+-:=&#/()<>,.?{}$@%*","ABCDEFGHIJKLMNOPQRSTUVWXYZ\x8E\x99\x9A*"};
    uint8_t charSet= 0; // currently active charset

   	void initGross();
   	void initKlein();
};

#endif /* SRC_DB_LCD_H_ */

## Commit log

2023-09-04 Update der Beschreibung für das Flashen.
2023-12-28 Add files via upload
    Schematics for microcontroller board
2023-12-28 update for microcontroller board
    added dsescription of coil connection
2024-01-02 schematics for sender and receiver device
2024-01-02 pictures of uC board sender side
2024-03-17 Add files via upload
    Änderungen für integration der Platine
    [Input_Bottom.stl, Input_Top.stl]
2024-04-17 Update Readme.md
    Liste der notwendigen Dateien für die webseite ergänzt.
